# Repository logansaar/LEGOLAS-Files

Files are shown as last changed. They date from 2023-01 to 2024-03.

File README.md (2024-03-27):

# LEGOLAS-Files
Repository for LEGOLAS use files

LEGOLAS is the **LEGO** Based **L**ow-cost **A**utonomous **S**cientist

Maryland_LEGOLAS (1)

Please refer to Chapter 2 of this [thesis](https://github.com/logansaar/LEGOLAS-Files/blob/main/Saar%20Thesis%20Final%20Document.pdf) for a top-level overview of LEGOLAS construction, setup, and use: 

For inquiries regarding Python templates and educational worksheets that address additional active learning schemas, please contact:  takeuchi@umd.edu, aaron.kusne@nist.gov

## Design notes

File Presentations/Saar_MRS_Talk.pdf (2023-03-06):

# A Low-Cost

# Education Platform for Teaching Autonomous Physical Science

# Logan Saar

University of Maryland & NIST | 1

## Ichiro Takeuchi, Gilad Kusne, Austin McDannald

Senior - Materials Science and Engineering, UMD (lsaar@umd.edu)

MRS Symposium on Accelerating Experimental Materials Research with Machine Learning

# CAMEO: Closed-Loop Autonomous Materials Exploration and Optimization

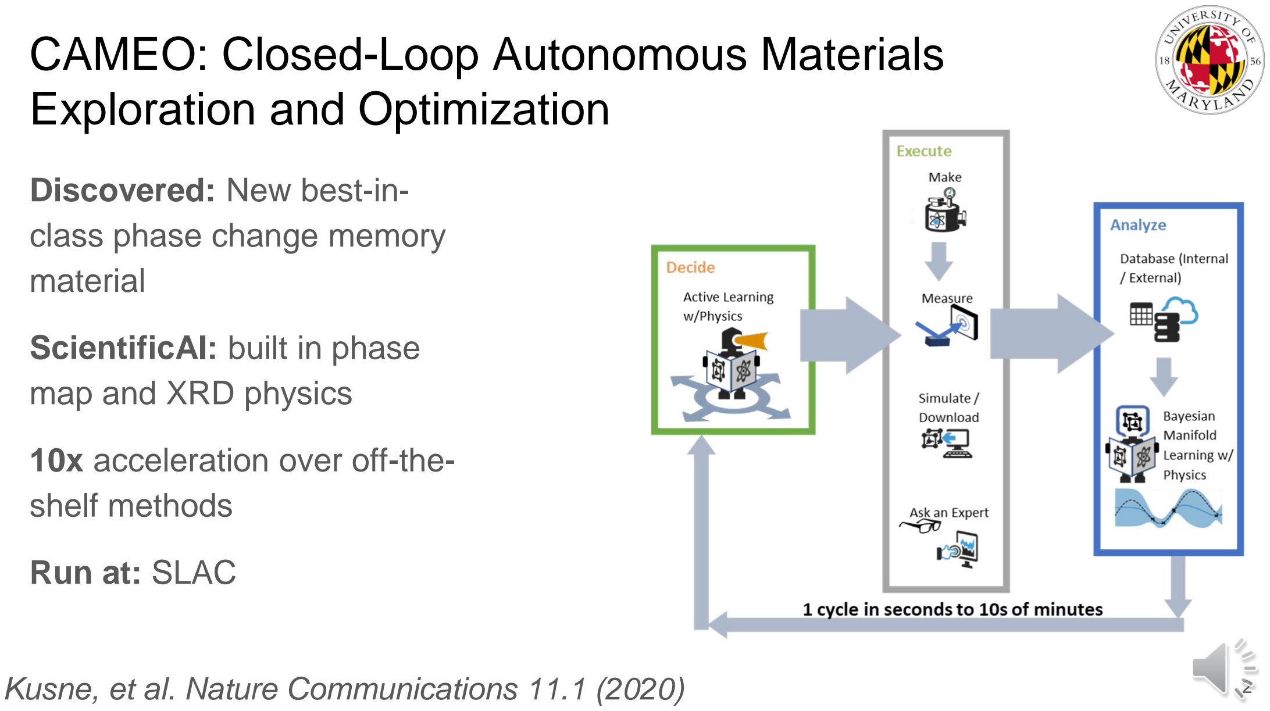
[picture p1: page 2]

## Discovered: New best-in-class phase change memory material

## ScientificAI: built in phase map and XRD physics

## 10x acceleration over off-the-shelf methods

## Run at: SLAC

### Kusne, et al. Nature Communications 11.1 (2020)

Burger, B., Maffettone, P.M., Gusev, V.V. et al. A mobile robotic chemist. Nature 583, 237–241 (2020)

Other Works

Stach, E., DeCost, B., Kusne, A. G., Hattrick-Simpers, J., Brown, K. A., Reyes, K. G., Schrier, J., Billinge, S., Buonassisi, T., Foster, I., Gomes, C. P., Gregoire, J. M., Mehta, A., Montoya, J., Olivetti, E., Park, C., Rotenberg, E., Saikin, S. K., Smullin, S., … Maruyama, B. (2021). Autonomous experimentation systems for materials development: A community perspective. Matter, 4(9), 2702-2726. https://doi.org/10.1016/j.matt.2021.06.036

# Low Cost Autonomous Physical Science System

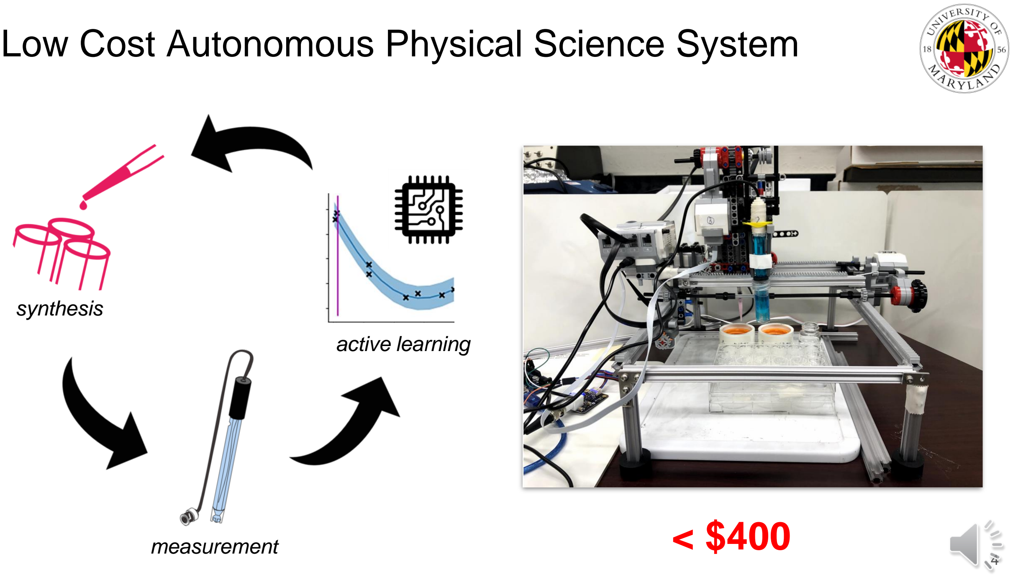
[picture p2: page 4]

measurement

synthesis

active learning

< $400

# Construction

Aluminum Frame

Lego Mindstorm
Components

Gerber, et al. (2017). Liquid-handling Lego robots and experiments for STEM education and research. PLOS Biology, 15(3)

# Synthesis Capabilities

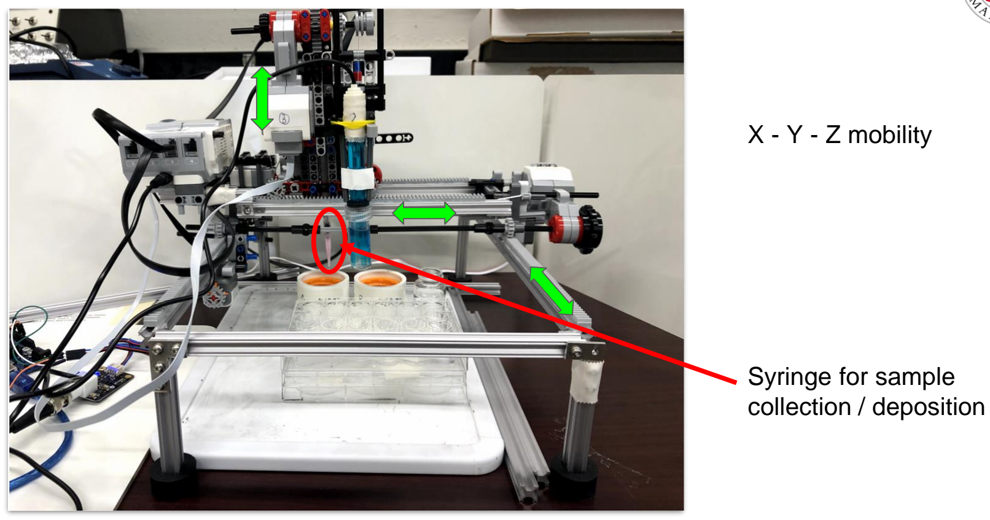
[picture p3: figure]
Syringe for sample collection / deposition; X - Y - Z mobility

# Measurement Capabilities

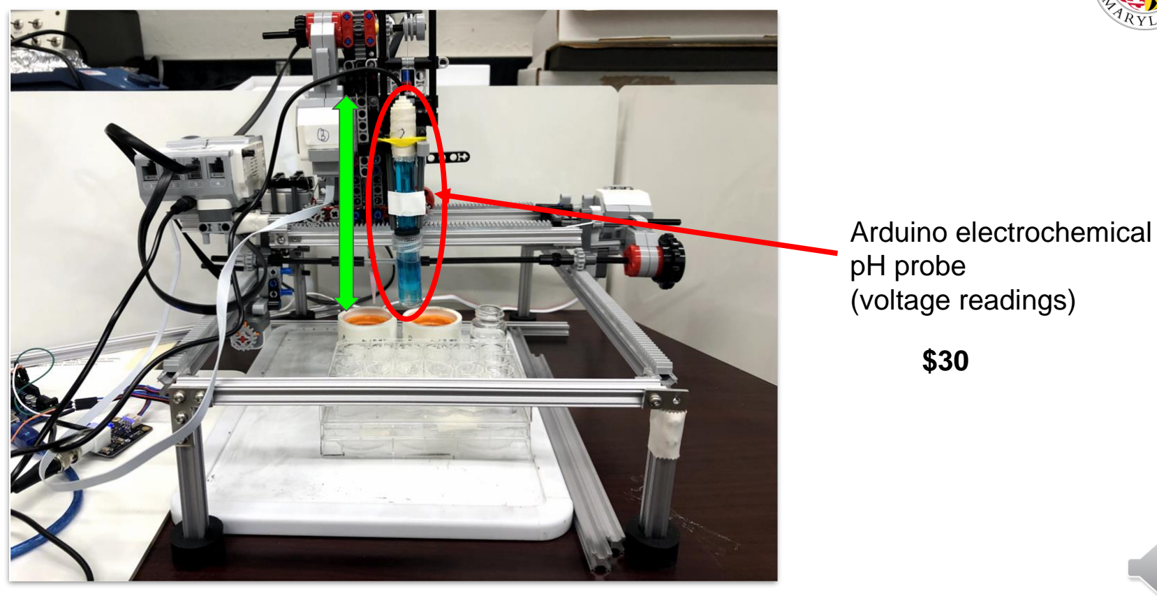
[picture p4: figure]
Arduino electrochemical pH probe (voltage readings)

# Setup and Control

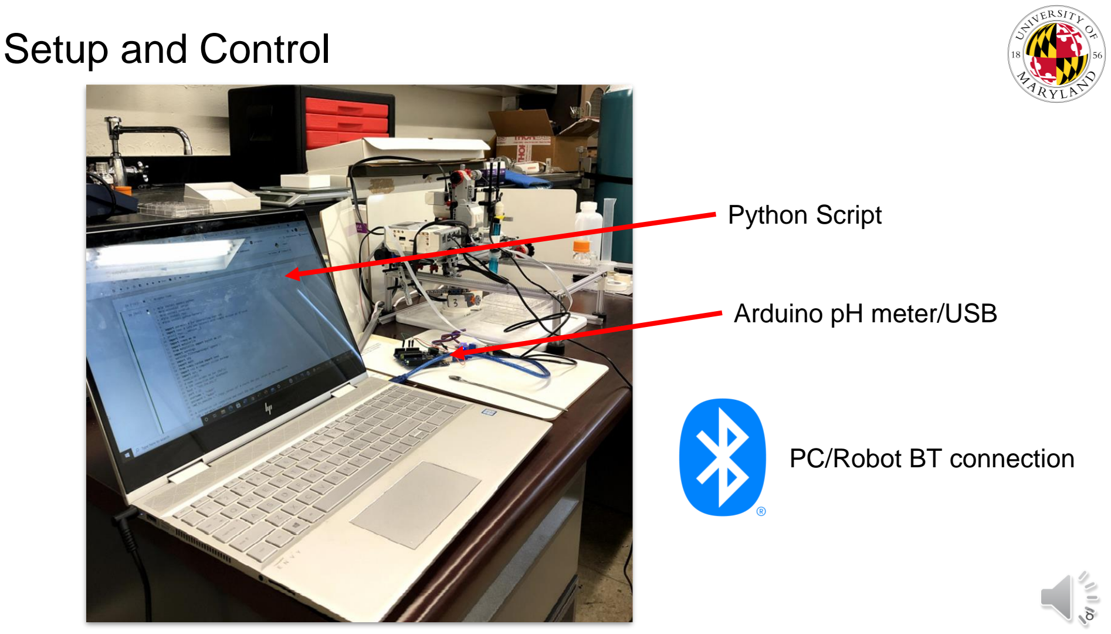
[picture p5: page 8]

Python Script

PC/Robot BT connection

Arduino pH meter/USB

# Exploring pH of Buffer Solutions

Composition Space
Weak Acid - Acetic Acid - 1 M
Conjugate Base - Sodium Acetate Solution - 1 M

Goal
Recover Henderson-Hasselbalch Equation.

## Henderson-Hasselbalch (HH) Equation:

Our known parameters
(for synthesis)

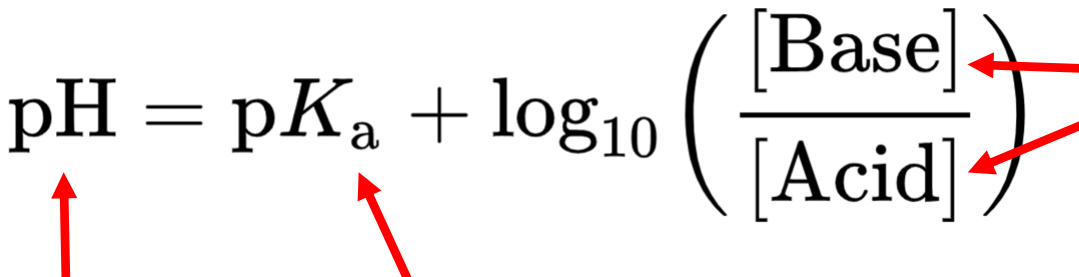
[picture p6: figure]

Response Variable
(measured)

Dissociation Constant
(unknown to robot)

# Active Learning Closed Loop System

- | Youtube Video Here | - (http://www.youtube.com/watch?v=Ul9sx29vAXE)

https://www.youtube.com/watch?v=Ul9sx29vAXE&t=1s

# Educational Application (Fall 2021 ENMA 437/637)

## UMD Machine Learning for Materials Science Course

## - 3 working systems - Teams of 5 students - Buffer Solution pH

- Gaussian Process
- Explore pH as f(composition)

## - Iodine Clock

# Model Determination

Can the Robot Determine the Physical Law by Itself?

# Can the Robot Discover the Physical Law?

## 1. Fit multiple functional forms to the data (“Candidates”)

## - (sinusoidal, power function, logarithmic, exponential, quadratic, etc.) - Non-linear least squares regression

x = [Acid]/[Base]

What is the correct form?

pH = A + B * log [C * (x-D) ] ? pH = A + B * sin [C * (x-D) ] ? pH = A + B * exp[C * (x-D) ] ? …

Alter parameters to get best fit

## 2. Create PDF for each candidate at every composition - (std. of PDF given by std. of residuals)

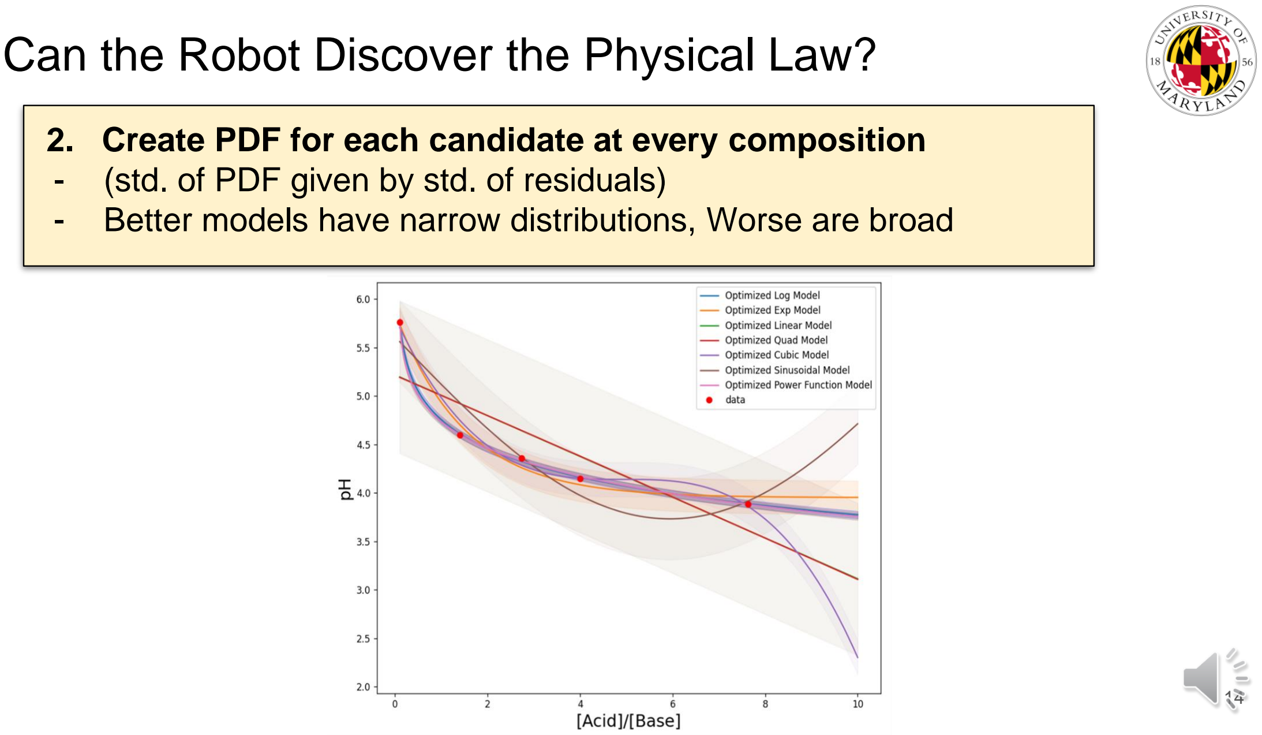
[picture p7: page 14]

## - Better models have narrow distributions, Worse are broad

# Can the Robot Discover the Physical Law?

## 3. Rank the likelihood that each candidate model produced the data

Performance Metric for
each candidate is the
sum of log(likelihood)
along every collected
data point

# Can the Robot Discover the Physical Law?

## 4. Determine which composition to measure next

# Yes, it did!

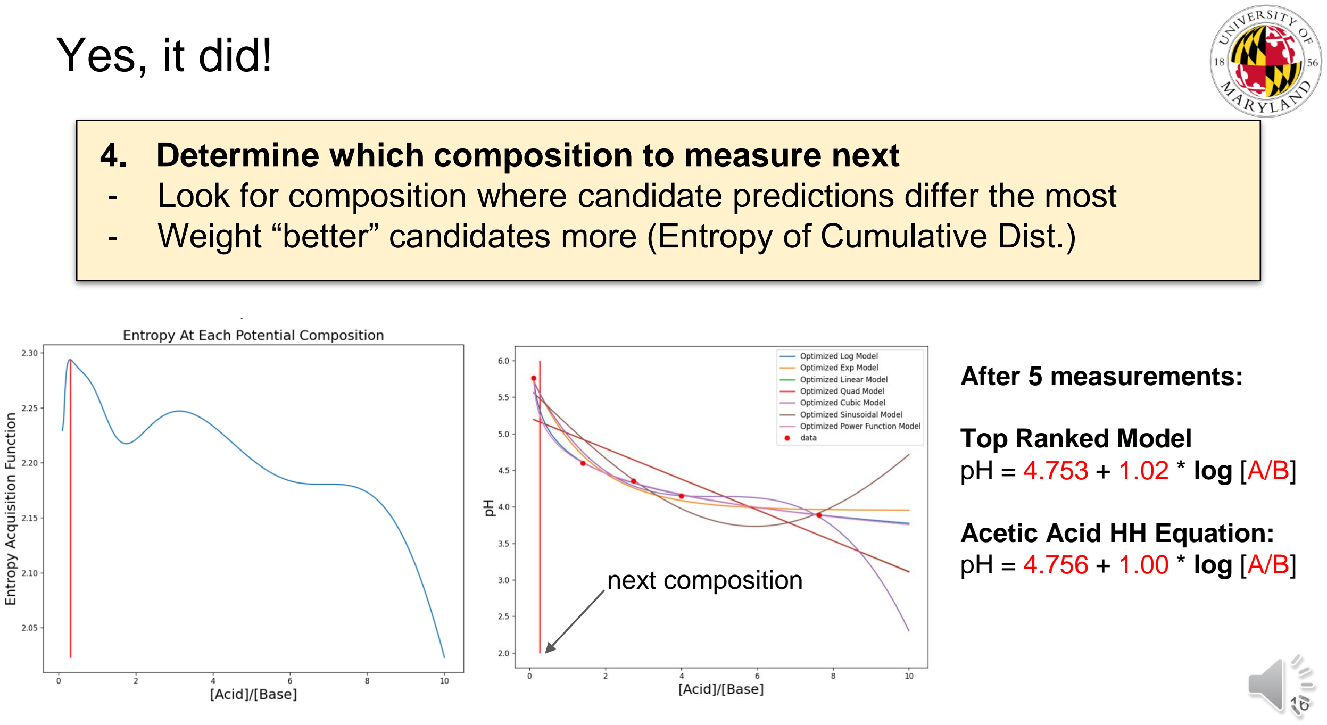
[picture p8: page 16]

## - Look for composition where candidate predictions differ the most - Weight “better” candidates more (Entropy of Cumulative Dist.)

next composition

After 5 measurements:

Top Ranked Model
pH = 4.753 + 1.02 * log [A/B]

Acetic Acid HH Equation:
pH = 4.756 + 1.00 * log [A/B]

# Summary

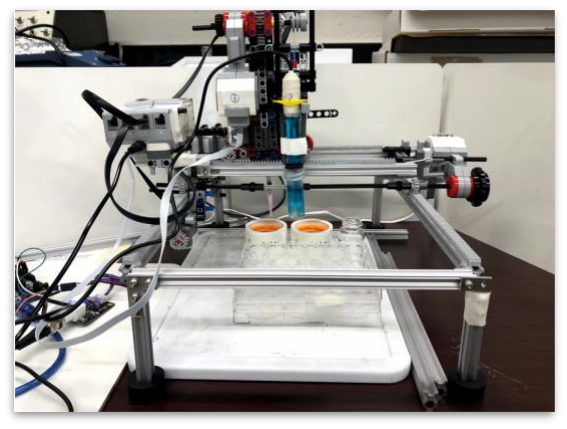
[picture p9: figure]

Closed Loop Autonomous Science System ➔ Educational Tool
➔ Low-cost
➔ Modular
➔ Materials Exploration

Used Gaussian Processes to explore pH as function of composition
➔ Flexible model
➔ Explore other active learning methods ...

# Acknowledgments

### Dr. Ichiro Takeuchi, PhD - UMD

### Dr. Gilad Kusne, PhD - NIST

### Dr. Austin McDannald, PhD - NIST

### Alex Wang - UMD

### Haotong Liang – UMD

### SURF Program – NIST

### MRS

## Email - lsaar@umd.edu

# References

Burger, B., Maffettone, P.M., Gusev, V.V. et al. A mobile robotic chemist. Nature 583, 237–241 (2020). https://doi.org/10.1038/s41586-020-2442-2

De Levie, R. (2003). The Henderson-hasselbalch equation: Its history and limitations. Journal of Chemical Education, 80(2), 146. https://doi.org/10.1021/ed080p146

Gerber, L. C., Calasanz-Kaiser, A., Hyman, L., Voitiuk, K., Patil, U., & Riedel-Kruse, I. H. (2017). Liquid-handling Lego robots and experiments for STEM education and research. PLOS Biology, 15(3), e2001413. https://doi.org/10.1371/journal.pbio.2001413

# Questions

# Appendix

## 4. Calculate the Entropy of the GMM at every composition

# Can the Robot Discover the Physical Law?

## - probability = (area under GMM likelihood curve)

## 4. Create a cumulative distribution of all PDFs at each composition

# Can the Robot Discover the Physical Law?

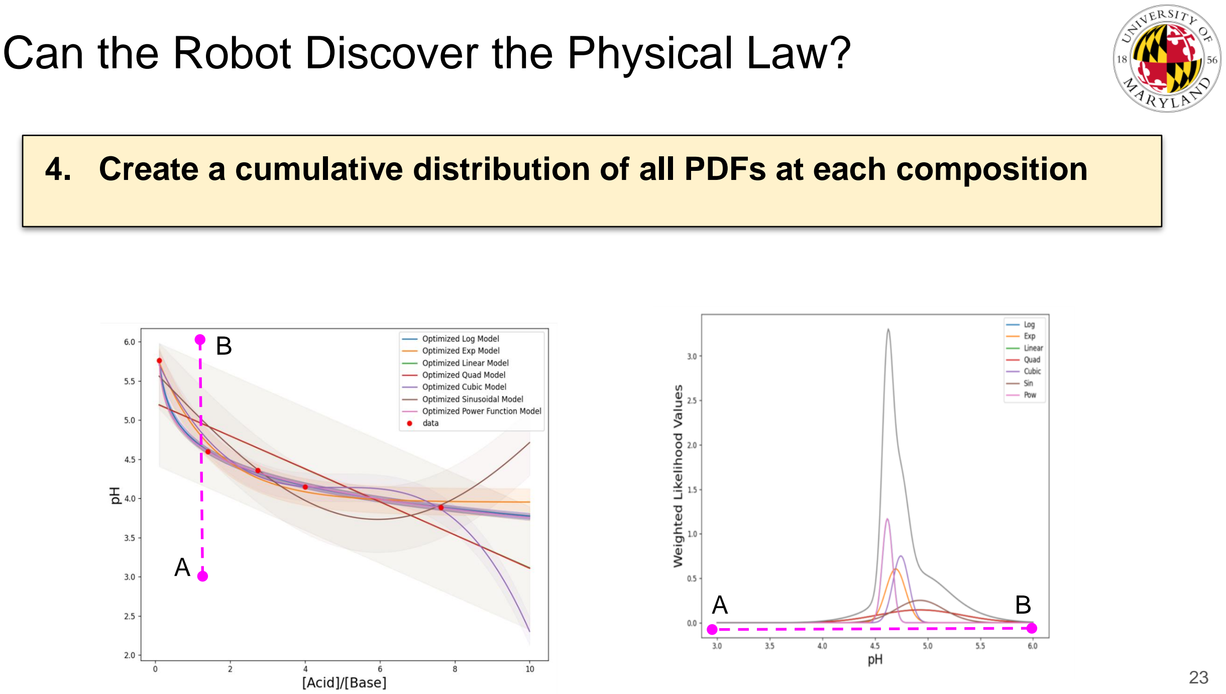
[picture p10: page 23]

A

B

A | B

# Exploration Initiative - (Gaussian Process)

Normal distribution of predicted pH for each potential % Acid composition

# Exploration Initiative - (Gaussian Process)

Kernel is a covariance function

# Exploration Initiative - (Gaussian Process)

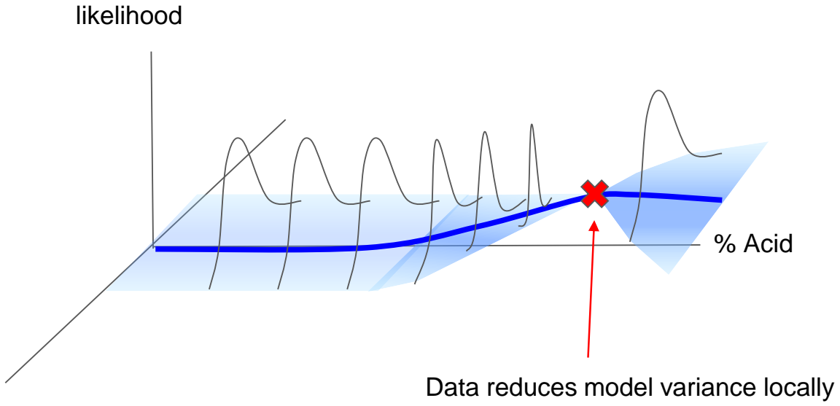
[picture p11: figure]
% Acid; likelihood; Data reduces model variance locally

pH

# Exploration Initiative - (Gaussian Process)

Active Learning:

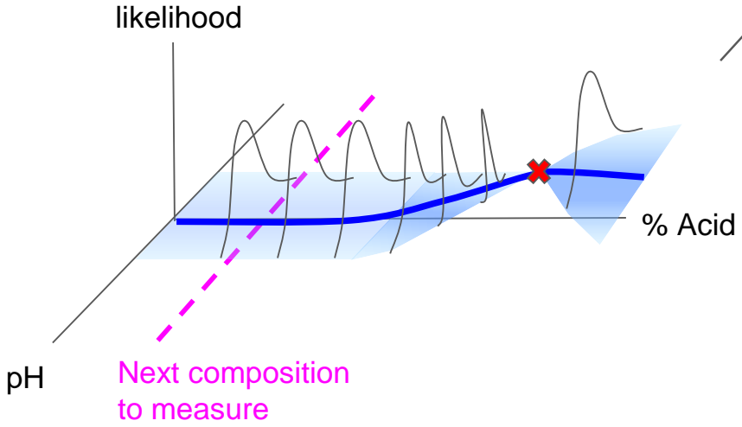
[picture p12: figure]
% Acid; likelihood; Next composition to measure

➔ Acquisition Function
➔ argmax (variance)
➔ Optimization initiative
➔ Scheduling of initiatives

# Autonomous Results - (Gaussian Process)

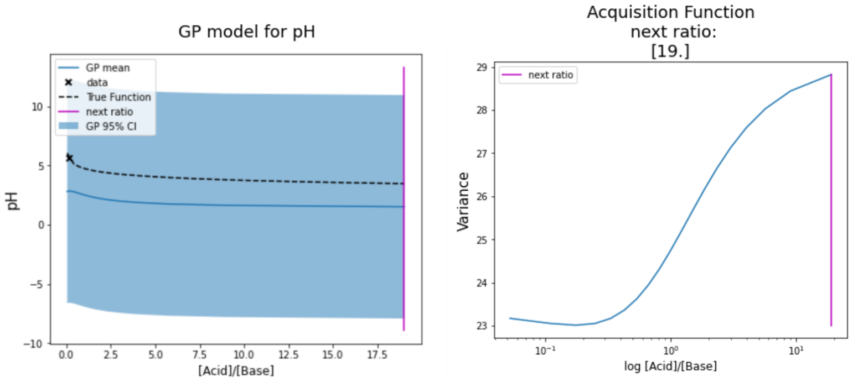
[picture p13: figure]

### 1 data point

# Autonomous Results - (Gaussian Process)

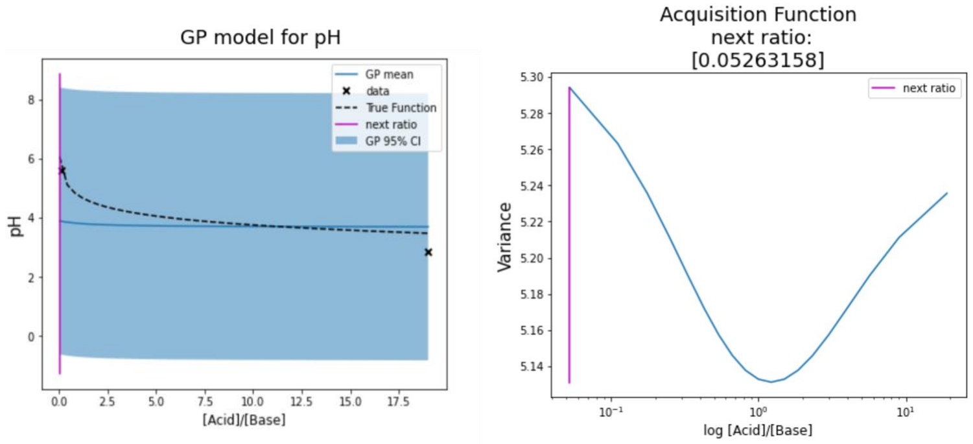
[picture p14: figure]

### 2 data points

# Autonomous Results - (Gaussian Process)

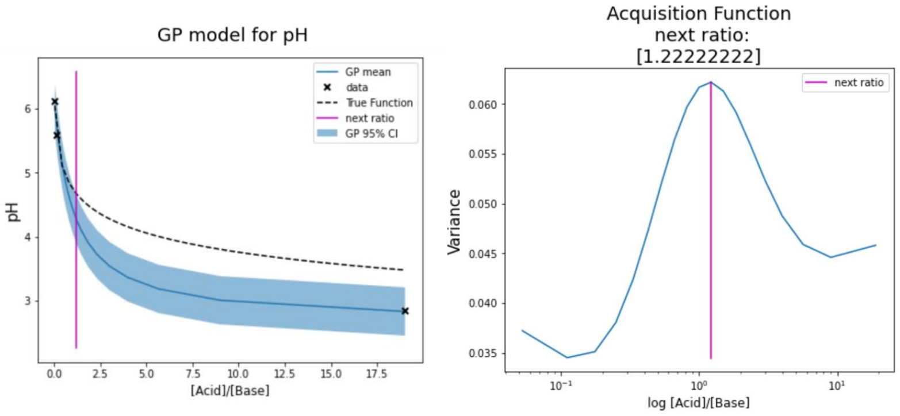
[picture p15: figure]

### 3 data points

# Autonomous Results - (Gaussian Process)

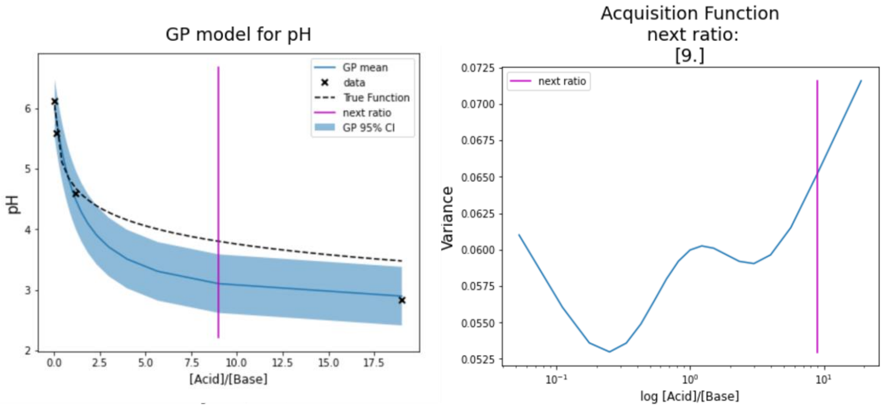
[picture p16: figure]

### 4 data points

# Autonomous Results - (Gaussian Process)

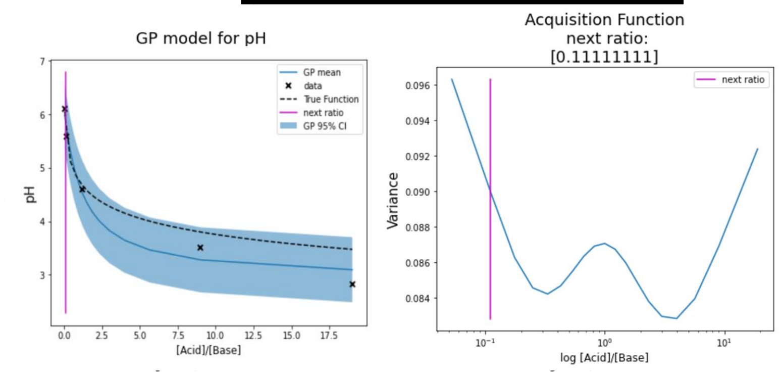
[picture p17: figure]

### 5 data points

# GP flexibility - (Gaussian Process)

HH equation relies on assumptions
➔ No self-ionization of water
➔ Valid only in certain composition range ➔ Our pKa ~ 4.7

# GP flexibility - (Gaussian Process)

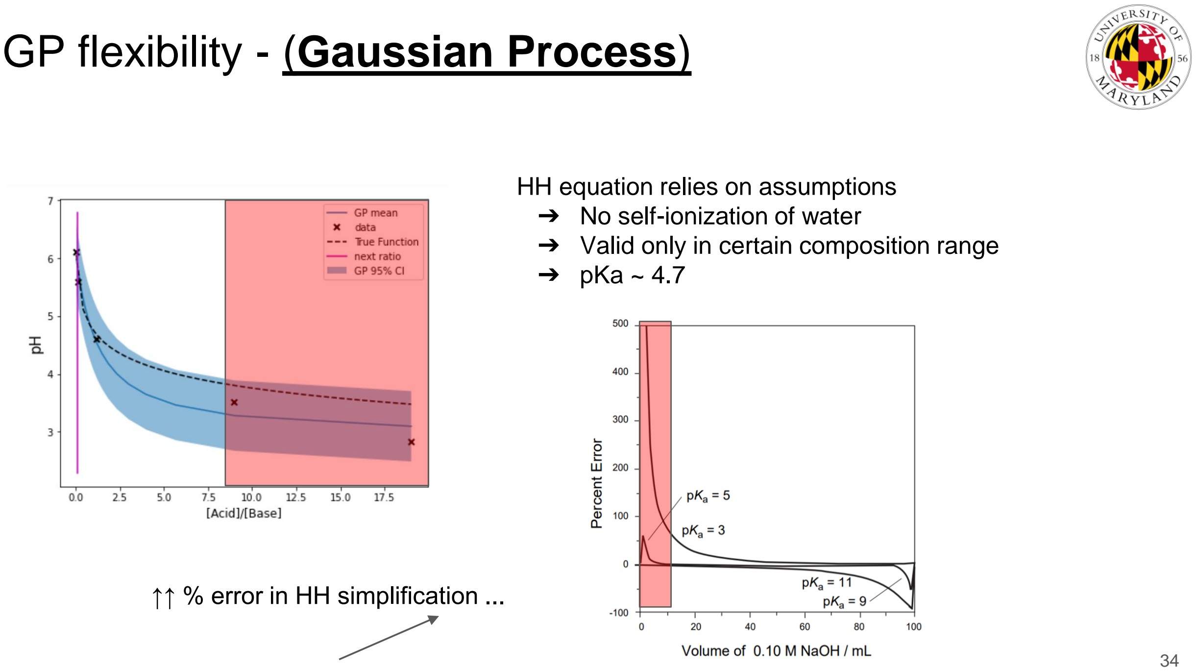
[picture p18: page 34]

HH equation relies on assumptions
➔ No self-ionization of water
➔ Valid only in certain composition range ➔ pKa ~ 4.7

↑↑ % error in HH simplification ...

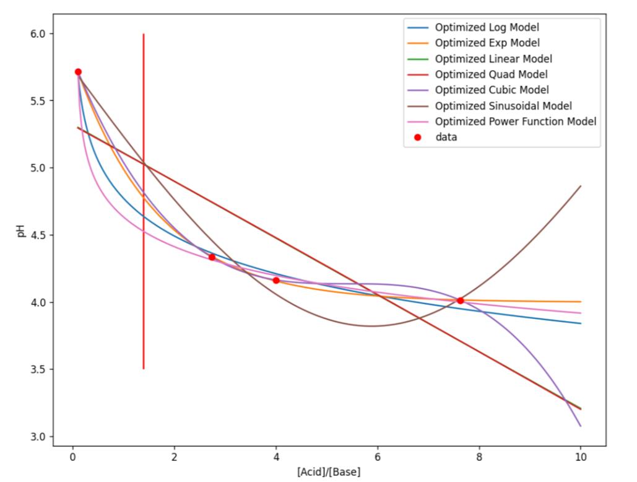
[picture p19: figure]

# Bayesian Inference

## Parameter Refinement

## Probabilistic interpretation … quantifying uncertainty (how confident are we?)

Bayes Theorem | P (model | data) = P(data | model) P(model) P(data)

# Brief Overview - Bayesian Machine Learning

## Probabilistic interpretation … quantifying uncertainty (how confident are we?)

Bayes Theorem | P (model | data) = P(data | model) P(model) P(data)

# Brief Overview - Bayesian Machine Learning

“Posterior” | “Prior”
Our confidence in this model being “correct” given the data (what we want to know) | Our confidence in this model being “correct” before getting data (assumption)

# Parameter Refinement - (Bayesian Inference)

## Prior: Assume model has logarithmic form (pH = A + B*log(C*x)) ➔ A, B, C are our model parameters

## Posterior: Probability of this model and its model parameters given the data

## Assume the model has a certain form

## Create parametric model with model parameters … (ex: model = A + B * x)

# Parameter Refinement - (Bayesian Inference)

## Problem: How to identify combination of parameters where posterior probability for model is greatest (i.e. best model?)

## Solution: Sample posterior distribution in parameter space using Markov Chain

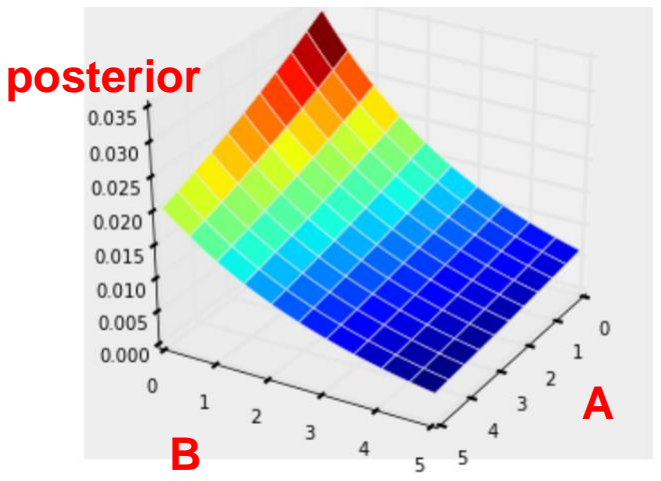
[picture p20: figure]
posterior

## Monte Carlo (MCMC) method A

Image Credit: https://nbviewer.jupyter.org/github/CamDavidsonPilon/Probabilistic-Programming-and-Bayesian-Methods-for-Hackers/blob/master/Chapter3_MCMC/Ch3_IntroMCMC_PyMC3.ipynb

## MCMC samples parameter space to find maxima in posterior (best model)

# Parameter Refinement - (Bayesian Inference)

## posterior

Example:

# Autonomous Results - (Bayesian Inference)

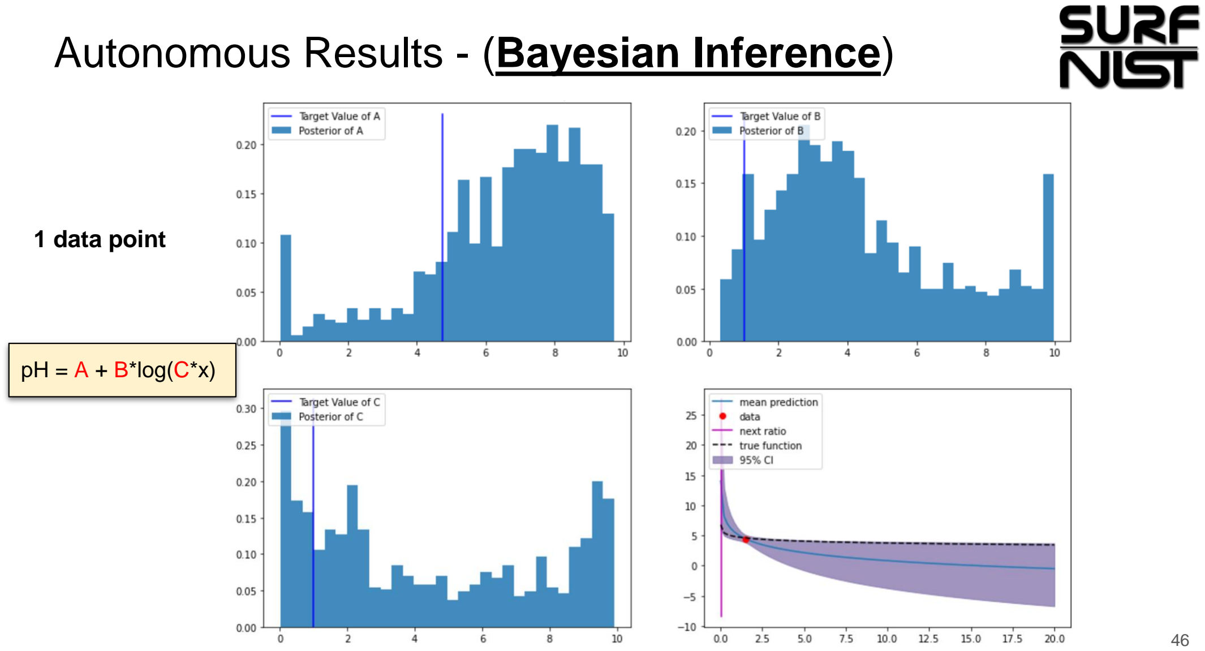
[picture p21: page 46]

### 1 data point

pH = A + B*log(C*x)

# Autonomous Results - (Bayesian Inference)

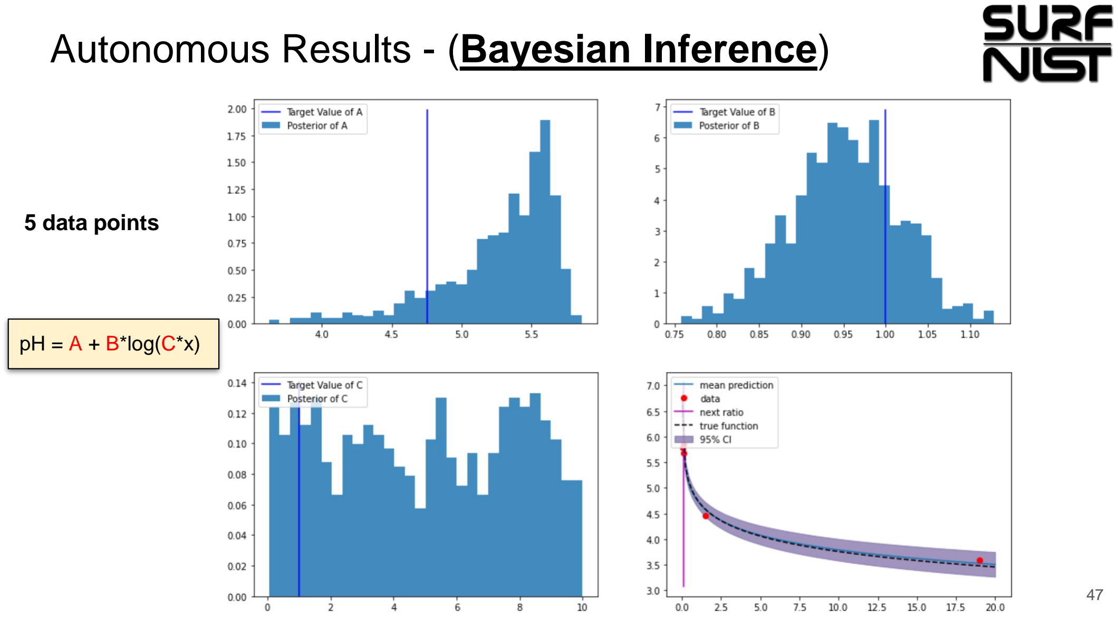
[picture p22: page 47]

### 5 data points

pH = A + B*log(C*x)

# The Next Steps:

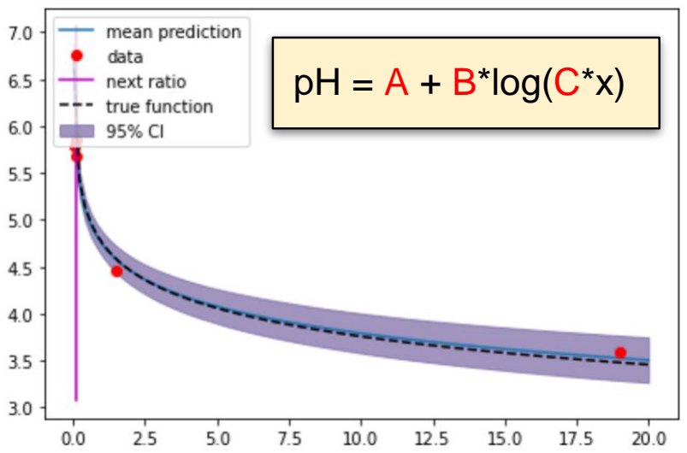
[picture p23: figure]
pH = A + B*log(C*x)

### For pH Measurement Setup

➔ Parameter Refinement

➔ Hypothesis Testing
➔ Bayesian methods
➔ Filter between candidate functions

## Other Applications (Educational Tool)

➔ Camera attachment
◆ Learn color mixing trends

## New data alters our prior beliefs → posterior beliefs

# Brief Overview - Bayesian Machine Learning

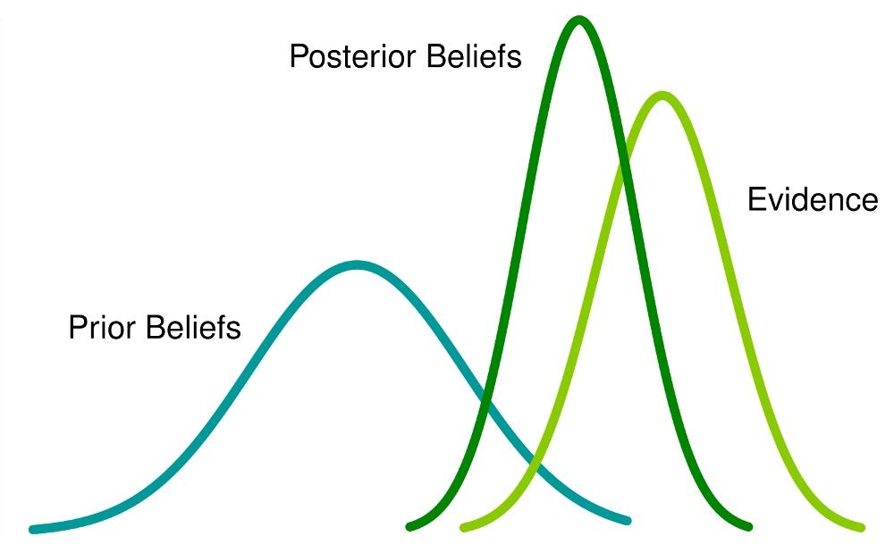
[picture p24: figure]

# Parameter Refinement - (Bayesian Inference)

## Produces posterior distributions for each model parameter

## Represent confidence in parameter values

## Active learning: [Parameter Refinement] → argmax (variance in model)

Example:

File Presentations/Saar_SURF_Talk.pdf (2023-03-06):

# Bayesian Active Learning for

# Autonomous Physical Science

# Logan Saar

Dr. Gilad Kusne (Mentor) - MML | 1

measurement

synthesis

active learning

# Motivation and Goals

# Composition - Property Relationships


### Optimize Performance → Properties → Composition

Image Credit: The four elements of materials science and engineering. (n.d.). https://www.nap.edu/read/758/chapter/3.

# Composition - Property Relationships

### Optimize Performance → Properties → Composition

Image Credit: The four elements of materials science and engineering. (n.d.). https://www.nap.edu/read/758/chapter/3.

# The Large Number Problem

σ

Element A
%B
0 | 50 | 100
Element B

# The Large Number Challenge


σ

Element A
%B
0 | 50 | 100
Element B

# The Large Number Challenge

σ

Element A
%B
0 | 50 | 100
Element B
Binary: | ~ 7,000
Tertiary: | ~ 250,000
Quaternary: ~ 7.6 million

Automated | Autonomous


Robot executes tasks | Robot reacts to input
Image Credit: https://blog.robotiq.com/a-brief-history-of-robots-in-manufacturing | Image Credit: Wired - Autonomous Cars

Automated | Autonomous

Robot reacts to ..
gathered data

ACTIVE LEARNING

Robot executes tasks


Burger, B., Maffettone, P.M., Gusev, V.V. et al. A mobile robotic chemist. Nature 583, 237–241 (2020)

# Low Cost Autonomous Physical Science System


11 measurement

synthesis

active learning

# Active Learning Closed Loop System

# Our Mission

Composition Space
Weak Acid - Acetic Acid - 1 M
Conjugate Base - Sodium Acetate Solution - 1 M

Goal
Recover Henderson-Hasselbalch Equation.

## Henderson-Hasselbalch (HH) Equation:

Our known parameters
(for synthesis)


Response Variable
(measured)

Dissociation Constant
(unknown to robot)

# Our Mission

Image Credit: https://www.easybiologyclass.com/titration-curve-of-a-weak-acid-and-its-pka-biochemistry-notes/

# Active Learning Closed Loop System - Our Robot

Aluminum Frame

## Construction

Lego Mindstorm
Components

Gerber, L. C. (2017). Liquid-handling Lego robots and experiments for STEM education and research. PLOS Biology, 15(3)

# Active Learning Closed Loop System - Our Robot

Syringe for sample collection / deposition (volume controlled); Sample Synthesis; X - Y - Z mobility

# Active Learning Closed Loop System - Our Robot

Measurement; Arduino electrochemical pH probe (voltage readings)

# Active Learning Closed Loop System - Our Robot

## Setup

Python Script

PC/Robot BT connection

Arduino pH meter/USB

# Active Learning Closed Loop System - Our Robot

## Process


Acid and base reservoirs

DI water (probe cleaning)

Plastic sample wells

# Active Learning Closed Loop System - Our Robot

Link Provided in Chat

- | Youtube Video Here | - (http://www.youtube.com/watch?v=Ul9sx29vAXE)

# Statistical Methods and Results

# Exploration Initiative - (Gaussian Process)

Normal distribution of predicted pH for each potential % Acid composition

% Acid; Likelihood of the model; 95% Confidence Interval; mean

# Exploration Initiative - (Gaussian Process)

pH

# Exploration Initiative - (Gaussian Process)

% Acid; likelihood; Next composition to measure

Active Learning:
➔ Acquisition Function
➔ argmax (variance)

# Autonomous Results - (Gaussian Process)


### 1 data point

# Autonomous Results - (Gaussian Process)


### 2 data points

# Autonomous Results - (Gaussian Process)


### 3 data points

# Autonomous Results - (Gaussian Process)


### 4 data points

# Autonomous Results - (Gaussian Process)


### 5 data points

# GP flexibility - (Gaussian Process)

HH equation relies on assumptions
➔ No self-ionization of water
➔ Valid only in certain composition range ➔ Our pKa ~ 4.7

# GP flexibility - (Gaussian Process)

HH equation relies on assumptions
➔ No self-ionization of water
➔ Valid only in certain composition range ➔ pKa ~ 4.7

↑↑ % error in HH simplification ...

# Summary


Closed Loop Autonomous Science System ➔ Educational Tool
➔ Low-cost
➔ Modular
➔ Materials Exploration

Used Gaussian Processes to explore pH as function of composition
➔ Flexible model
➔ Explore other active learning methods ...

# Acknowledgments

### Dr. Gilad Kusne, PhD

### Dr. Ichiro Takeuchi, PhD

### Dr. Austin McDannald, PhD

### Alex Wang

### Haotong Liang

# Questions

# References

Burger, B., Maffettone, P.M., Gusev, V.V. et al. A mobile robotic chemist. Nature 583, 237–241 (2020). https://doi.org/10.1038/s41586-020-2442-2

De Levie, R. (2003). The Henderson-hasselbalch equation: Its history and limitations. Journal of Chemical Education, 80(2), 146. https://doi.org/10.1021/ed080p146

Gerber, L. C., Calasanz-Kaiser, A., Hyman, L., Voitiuk, K., Patil, U., & Riedel-Kruse, I. H. (2017). Liquid-handling Lego robots and experiments for STEM education and research. PLOS Biology, 15(3), e2001413. https://doi.org/10.1371/journal.pbio.2001413

# Appendix

# The Next Steps:

pH = A + B*log(C*x)

### For pH Measurement Setup

➔ Parameter Refinement

➔ Hypothesis Testing
➔ Bayesian methods
➔ Filter between candidate functions

## Other Applications (Educational Tool)

➔ Camera attachment
◆ Learn color mixing trends

# Exploration Initiative - (Gaussian Process)

% Acid; Likelihood of the model; mean; Many models generated: ➔ Non-parametric ➔ Flexible ➔ Averaged ➔ Kernel determines “smoothness” ➔ Noise tolerant

Kernel is a covariance function

## Probabilistic interpretation … quantifying uncertainty (how confident are we?)

Bayes Theorem | P (model | data) = P(data | model) P(model) P(data)

# Brief Overview - Bayesian Machine Learning

## Probabilistic interpretation … quantifying uncertainty (how confident are we?)

Bayes Theorem | P (model | data) = P(data | model) P(model) P(data)

# Brief Overview - Bayesian Machine Learning

“Posterior” | “Prior”
Our confidence in this model being “correct” given the data (what we want to know) | Our confidence in this model being “correct” before getting data (assumption)

## New data alters our prior beliefs → posterior beliefs

# Brief Overview - Bayesian Machine Learning

## Assume the model has a certain form Create parametric model with model parameters … (ex: model = A + B * x)

# Parameter Refinement - (Bayesian Inference)

## Problem: How to identify combination of parameters where posterior probability for model is greatest (i.e. best model?)

## Solution: Sample posterior distribution in parameter space using Markov Chain

posterior

## Monte Carlo (MCMC) method A

Image Credit: https://nbviewer.jupyter.org/github/CamDavidsonPilon/Probabilistic-Programming-and-Bayesian-Methods-for-Hackers/blob/master/Chapter3_MCMC/Ch3_IntroMCMC_PyMC3.ipynb

## MCMC samples parameter space to find maxima in posterior (best model)

# Parameter Refinement - (Bayesian Inference)

## posterior

Example:

# Parameter Refinement - (Bayesian Inference)

## Produces posterior distributions for each model parameter

Posterior of A; Posterior of B

## Represent confidence in parameter values

## Active learning: [Parameter Refinement] → argmax (variance in model)

Example:

# Parameter Refinement - (Bayesian Inference)

## Prior: Assume model has logarithmic form (pH = A + B*log(C*x))

## Posterior: Probability of this model and its model parameters given the data

# Autonomous Results - (Bayesian Inference)


### 1 data point

pH = A + B*log(C*x)

# Autonomous Results - (Bayesian Inference)


### 5 data points

pH = A + B*log(C*x)

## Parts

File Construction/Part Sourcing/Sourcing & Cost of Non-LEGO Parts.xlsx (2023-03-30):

Vendor | Description | URL | Unit Price ($) | Quantity | Net Price | Summary
MakerBeam | 300 mm Anodised Al Extrusion (Black - 4 piece) | https://www.makerbeam.com/makerbeam-300mm-4p-black-makerbeam.html | $12.03 | 2 | $24.07 | Frame Components ... Price per Robot ~ $100
MakerBeam | 3D printed End Caps (Black - 4 piece) | https://www.makerbeam.com/makerbeam-3d-printed-end-caps-for-makerbeam-4p.html?id=24117793 | $4.99 | 1 | $4.99
MakerBeam | Corner Cubes (Black - 12 piece w/ screws) | https://www.makerbeam.com/makerbeam-corner-cubes-12p-black-for-makerbeam.html?id=24117589 | $18.85 | 1 | $18.85
MakerBeam | 90 degree L-Brackets (12-piece) | https://www.makerbeam.com/makerbeam-90-degree-brackets-12p.html?id=24117637 | $7.30 | 1 | $7.30
MakerBeam | T-slot Nuts (25-piece) | https://www.makerbeam.com/makerbeam-t-slot-nuts-for-makerbeam-25p.html?id=24117835 | $15.73 | 2 | $31.46
MakerBeam | 6-mm M3 Wing Bolts (100 pack) | https://www.makerbeam.com/makerbeam-wing-type-bolts-6mm-100p-for-makerbeam.html | $11.53 | 1 | $11.53
CanaKit | R-Pi Buildhat | https://www.canakit.com/raspberry-pi-build-hat.html | $25 | 2 | $50 | Non-Lego Electronics ... Price per Robot ~ $470
DigiKey | R-Pi Buildhat Chargers (Australian Plug) | https://www.digikey.com/en/products/detail/raspberry-pi/SC0749/15298150?src=raspberrypi | $15 | 2 | $30
DF Robot | Arduino pH Sensors | https://www.dfrobot.com/product-1025.html | $29.50 | 1 | $29.50
Amazon | R-Pi 4GB 64 bit | https://www.amazon.com/CanaKit-Raspberry-Pi-Extreme-Kit/dp/B09W7P91SP?hvadid=598359365939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 | $139.99 | 2 | $279.98
Amazon | Plug Adapter (US - Aus) | https://www.amazon.com/Unidapt-Adapter-Grounded-Adaptor-Converter/dp/B08D741PV6?hvadid=459618435588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 | $7.99 | 2 | $15.98
Amazon | Arduino Uno | https://www.amazon.com/gp/product/B008GRTSV6?camp=1789&creative=9325&creativeASIN=B008GRTSV6&linkId=d7b55cbe1aae09827d7c156218cf0efb | $28.50 | 1 | $28.50
Amazon | USB 2.0 A Male to B Male | https://www.amazon.com/Monoprice-1-5-Feet-24AWG-Plated-105436/dp/B009GUVZOK?hvadid=309773039951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 | $3.96 | 1 | $3.96
Amazon | Digital Scale (mg accuracy) | https://www.amazon.com/Milligram-Calibration-Tweezers-Weighing-Included/dp/B09NQ4RGHC?hvadid=564700665543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 | $18.58 | 1 | $18.58
Amazon | Jumper Wire Cables | https://www.amazon.com/Practical-Durable-Breadboard-Connecting-Prototyping/dp/B09XDL1JFG | $3.37 | 1 | $3.37
Ali Express | WeDo Extension Cables for LEGO | https://www.aliexpress.us/item/3256801836960111.html?_t=pvid%3Ab7549926-05dc-4d5d-8cc6-c14974441944&_randl_shipto=US | $6.11 | 1 | $6.11
Amazon | Chem Lab Stands and Rings (1 pack) | https://www.amazon.com/QWORK-Laboratory-Stands-Support-Burette/dp/B08ZSC1H5F | $19.97 | 1 | $19.97 | Chemistry Equipment ... Price per Robot ~ $40
Amazon | 1 mL/cc syringes (10 pack) | https://www.amazon.com/Measuring-Individually-Measurement-Scientific-Applicator/dp/B08T175QFR?s=industrial | $6.99 | 1 | $6.99
Adh. Disp. LTD | 20 guage dispensing tips (50 pack) | https://www.adhesivedispensing.net/TN20_Tapered_Tip_pink_pk_50_p/tn20.htm | $10.00 | 1 | $10.00
NEST | 24 Well Cell Culture Plates (~1cm diameter) | https://www.nest-biotech.com/cell-culture-plates/59174695.html | $5.00 | 1 | $5.00
 |  |  |  | Cost Per Robot | $584.14

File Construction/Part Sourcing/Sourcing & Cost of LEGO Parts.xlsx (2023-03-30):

LdrawID | Part | Color | Qty | Total Price | Link
11955 | Technic, Gear 8 Tooth with Dual Face without Friction | Dark Gray | 1 | $0.35 | https://www.lego.com/en-us/pick-and-build/pick-a-brick?query=11955&page=1
13971 | Wheel 18mm D. x 8mm with Fake Bolts and Deep Spokes with Inner Ring | Light Bluish Gray | 1 | $0.20 | https://www.lego.com/en-us/pick-and-build/pick-a-brick?query=13971&page=1
15100 | Technic, Pin with Friction Ridges and Pin Hole | White | 1 | $0.22 | https://www.toypro.com/us/product/35713/technic-pin-with-friction-ridges-lengthwise-and-pin-hole/white
24316 | Technic, Axle 3L with Stop | Reddish Brown | 3 | $0.21 | https://www.lego.com/en-us/pick-and-build/pick-a-brick?query=24316&page=1
2780 | Technic, Pin with Short Friction Ridges | Black | 64 | $3.84 | https://www.lego.com/en-us/pick-and-build/pick-a-brick?query=2780&page=1
32009 | Technic, Liftarm, Modified Bent Thick 1 x 11.5 Double | Light Bluish Gray | 2 | $0.70 | https://www.toypro.com/us/product/481/technic-liftarm-1-x-11-5-double-bent-thick/light-bluish-gray
32073 | Technic, Axle 5L | White | 1 | $0.11 | https://www.lego.com/en-us/pick-and-build/pick-a-brick?query=32073&page=1
32073 | Technic, Axle 5L | Black | 1 | $0.11 | https://www.lego.com/en-us/pick-and-build/pick-a-brick?query=32073&page=1
4265c | Technic Bush 1/2 Smooth | Light Bluish Gray | 2 | $0.10 | https://www.toypro.com/us/product/1966/technic-bush-1-2-smooth/light-bluish-gray
44 | Technic, Axle and Pin Connector Toggle Joint Smooth | Red (Link is White) | 1 | $0.50 | https://www.toypro.com/us/product/26390/technic-axle-and-pin-connector-toggle-joint-smooth/white
32140 | Technic, Liftarm, Modified Bent Thick L-Shape 2 x 4 | White (Link is Bluish Gray) | 3 | $0.42 | https://www.toypro.com/us/product/1125/technic-liftarm-2-x-4-l-shape-thick/light-bluish-gray
32140 | Technic, Liftarm, Modified Bent Thick L-Shape 2 x 4 | Light Bluish Gray | 2 | $0.28 | https://www.toypro.com/us/product/1125/technic-liftarm-2-x-4-l-shape-thick/light-bluish-gray
32184 | Technic, Axle and Pin Connector Perpendicular 3L with Center Pin Hole | Black | 4 | $0.56 | https://www.toypro.com/us/product/1395/technic-axle-and-pin-connector-perpendicular-3l-with-center-pin-hole/black
32269 | Technic, Gear 20 Tooth Double Bevel | Tan | 4 | $1.84 | https://www.toypro.com/us/product/1506/technic-gear-20-tooth-double-bevel/tan
32270 | Technic, Gear 12 Tooth Double Bevel | Light Bluish Gray | 4 | $0.72 | https://www.lego.com/en-us/pick-and-build/pick-a-brick?query=32270&page=1
32278 | Technic, Liftarm Thick 1 x 15 | White (Link is Bluish Gray) | 3 | $1.98 | https://www.toypro.com/us/product/1483/technic-liftarm-1-x-15-thick/dark-bluish-gray
32278 | Technic, Liftarm Thick 1 x 15 | Light Bluish Gray (Link is Dark Grey) | 1 | $0.66 | https://www.toypro.com/us/product/1483/technic-liftarm-1-x-15-thick/dark-bluish-gray
32316 | Technic, Liftarm Thick 1 x 5 | Black | 1 | $0.19 | https://www.lego.com/en-us/pick-and-build/pick-a-brick?query=32316&page=1
32316 | Technic, Liftarm Thick 1 x 5 | Light Bluish Gray | 3 | $0.57 | https://www.lego.com/en-us/pick-and-build/pick-a-brick?query=32316&page=1
32523 | Technic, Liftarm Thick 1 x 3 | Black | 3 | $0.30 | https://www.lego.com/en-us/pick-and-build/pick-a-brick?query=32523&page=1
32523 | Technic, Liftarm Thick 1 x 3 | White | 3 | $0.30 | https://www.lego.com/en-us/pick-and-build/pick-a-brick?query=32523&page=1
32523 | Technic, Liftarm Thick 1 x 3 | Light Bluish Gray | 1 | $0.10 | https://www.lego.com/en-us/pick-and-build/pick-a-brick?query=32523&page=1
32524 | Technic, Liftarm Thick 1 x 7 | Black | 1 | $0.25 | https://www.lego.com/en-us/pick-and-build/pick-a-brick?query=32524&page=1
32524 | Technic, Liftarm Thick 1 x 7 | White | 2 | $0.50 | https://www.lego.com/en-us/pick-and-build/pick-a-brick?query=32524&page=1
32524 | Technic, Liftarm Thick 1 x 7 | Light Bluish Gray | 3 | $0.75 | https://www.lego.com/en-us/pick-and-build/pick-a-brick?query=32524&page=1
32525 | Technic, Liftarm Thick 1 x 11 | White | 2 | $0.76 | https://www.toypro.com/us/product/4719/technic-liftarm-1-x-11-thick/white
32526 | Technic, Liftarm, Modified Bent Thick L-Shape 3 x 5 | Black | 7 | $1.68 | https://www.lego.com/en-us/pick-and-build/pick-a-brick?query=32526&page=1
32526 | Technic, Liftarm, Modified Bent Thick L-Shape 3 x 5 | White | 1 | $0.24 | https://www.lego.com/en-us/pick-and-build/pick-a-brick?query=32526&page=1
3707 | Technic, Axle 8L | White | 2 | $0.44 | https://www.lego.com/en-us/pick-and-build/pick-a-brick?query=3707&page=1
3708 | Technic, Axle 12L | Black | 11 | $2.97 | https://www.lego.com/en-us/pick-and-build/pick-a-brick?query=3708&page=1
3713 | Technic Bush | Light Bluish Gray | 13 | $1.30 | https://www.toypro.com/us/product/968/technic-bush/light-bluish-gray
37312c01 | Electric Sensor, Force - SPIKE Prime | Black | 2 | $63.90 | https://education.lego.com/en-us/products/lego-technic-force-sensor/45606?s_kwcid=AL!790!3!!!!x!!&mtm_medium=SEM
3743 | Technic, Gear Rack 1 x 4 | Light Bluish Gray | 43 | $8.17 | https://www.lego.com/en-us/pick-and-build/pick-a-brick?query=3743&page=1
3749 | Technic, Axle 1L with Pin without Friction Ridges | Tan | 2 | $0.14 | https://www.toypro.com/us/product/1152/technic-axle-pin-without-friction-ridges-lengthwise/tan
39367c02 | Wheel 56 x 14 Technic with Axle Hole and 8 Pin Holes with Fixed Black Rubber Tire | Black | 1 | $2.76 | https://www.toypro.com/us/product/40878/wheel-56-x-14-technic-with-axle-hole-and-8-pin-holes-with-fixed-black-rubber-tire/black
39790 | Technic, Liftarm, Modified Frame Thick 11 x 15 Open Center | Black | 1 | $2.14 | https://www.lego.com/en-us/pick-and-build/pick-a-brick?query=39790&page=1
41239 | Technic, Liftarm Thick 1 x 13 | Light Bluish Gray | 2 | $0.78 | https://www.lego.com/en-us/pick-and-build/pick-a-brick?query=41239&page=1&filters.i0.values.i0=pab
42003 | Technic, Axle and Pin Connector Perpendicular 3L with 2 Pin Holes | Red | 2 | $0.38 | https://www.toypro.com/us/product/3449/technic-axle-and-pin-connector-perpendicular-3l-with-2-pin-holes/red
42003 | Technic, Axle and Pin Connector Perpendicular 3L with 2 Pin Holes | Black | 2 | $0.28 | https://www.toypro.com/us/product/1916/technic-axle-and-pin-connector-perpendicular-3l-with-2-pin-holes/black
43093 | Technic, Axle 1L with Pin with Friction Ridges | Blue | 8 | $0.88 | https://www.toypro.com/us/product/1664/technic-axle-pin-with-friction-ridges-lengthwise/blue
44294 | Technic, Axle 7L | Light Bluish Gray | 2 | $0.32 | https://www.lego.com/en-us/pick-and-build/pick-a-brick?query=44294&page=1&filters.i0.values.i0=pab
4519 | Technic, Axle 3L | White | 1 | $0.05 | https://www.lego.com/en-us/pick-and-build/pick-a-brick?query=4519&page=1
48989 | Technic, Pin Connector Perpendicular 3L with 4 Pins | Light Bluish Gray | 9 | $1.80 | https://www.toypro.com/us/product/1928/technic-pin-connector-perpendicular-3l-with-4-pins/light-bluish-gray
54696c01 | Electric, Motor SPIKE Prime, Medium Angular | Light Bluish Gray | 5 | $214.75 | https://education.lego.com/en-us/products/lego-technic-medium-angular-motor/45603?s_kwcid=AL!790!3!!!!x!!&mtm_medium=SEM
56903 | Wheel 18mm D. x 8mm with Fake Bolts and Shallow Spokes and Axle Hole | White | 1 | $0.32 | https://www.lego.com/en-us/pick-and-build/pick-a-brick?query=56903&page=1
6538c | Technic, Axle Connector 2L (Smooth with x Hole + Orientation) | White | 7 | $1.26 | toypro.com/us/product/36700/technic-axle-connector-smooth-with-x-hole-orientation/white
60479 | Plate 1 x 12 | White | 1 | $0.23 | https://www.lego.com/en-us/pick-and-build/pick-a-brick?query=60479&page=1
60484 | Technic, Liftarm, Modified T-Shape Thick 3 x 3 | White | 1 | $0.18 | https://www.lego.com/en-us/pick-and-build/pick-a-brick?query=60484&page=1
60485 | Technic, Axle 9L | Yellow | 2 | $0.40 | https://www.lego.com/en-us/pick-and-build/pick-a-brick?query=60485&page=1
63869 | Technic, Axle and Pin Connector Perpendicular Triple | Light Bluish Gray | 2 | $0.46 | https://www.toypro.com/us/product/1452/technic-axle-and-pin-connector-perpendicular-triple/light-bluish-gray
64178 | Technic, Liftarm, Modified Frame Thick 5 x 11 Open Center | Light Bluish Gray | 1 | $1.24 | https://www.lego.com/en-us/pick-and-build/pick-a-brick?query=64178&page=1
64179 | Technic, Liftarm, Modified Frame Thick 5 x 7 Open Center | Light Bluish Gray | 4 | $3.56 | https://www.lego.com/en-us/pick-and-build/pick-a-brick?query=64179&page=1
64179 | Technic, Liftarm, Modified Frame Thick 5 x 7 Open Center | Black | 1 | $0.89 | https://www.lego.com/en-us/pick-and-build/pick-a-brick?query=64179&page=1
64781 | Technic, Gear Rack 1 x 13 with Axle and Pin Holes | Black | 2 | $4.20 | https://www.toypro.com/us/product/2322/technic-gear-rack-1-x-13-with-axle-and-pin-holes/black
6536 | Technic, Axle and Pin Connector Perpendicular | Red | 1 | $0.15 | https://www.toypro.com/us/product/1008/technic-axle-and-pin-connector-perpendicular/red
6558 | Technic, Pin 3L with Friction Ridges | Blue | 30 | $1.80 | https://www.lego.com/en-us/pick-and-build/pick-a-brick?query=6558&page=1
87082 | Technic, Pin 3L with Friction Ridges and Center Pin Hole | Light Bluish Gray | 2 | $0.36 | https://www.toypro.com/us/product/2210/technic-pin-long-with-friction-ridges-lengthwise-and-center-pin-hole/light-bluish-gray
94925 | Technic, Gear 16 Tooth (Second Version - Reinforced) | Light Bluish Gray | 12 | $2.40 | https://www.lego.com/en-us/pick-and-build/pick-a-brick?query=94925&page=1
 |  |  | Total: | $336.95

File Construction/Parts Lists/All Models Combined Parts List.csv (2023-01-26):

BLItemNo | ElementId | LdrawId | PartName | BLColorId | LDrawColorId | ColorName | ColorCategory | Qty | Weight
11955 |  | 11955 | Technic, Gear 8 Tooth with Dual Face without Friction | 10 | 8 | Dark Gray | Solid Colors | 1 | 0.2
13971 | 6044729 | 13971 | Wheel 18mm D. x 8mm with Fake Bolts and Deep Spokes with Inner Ring | 86 | 71 | Light Bluish Gray | Solid Colors | 1 | 1.02
15100 | 6282148 | 15100 | Technic, Pin with Friction Ridges and Pin Hole | 1 | 15 | White | Solid Colors | 1 | 0.4
24316 | 6135494 | 24316 | Technic, Axle 3L with Stop | 88 | 70 | Reddish Brown | Solid Colors | 3 | 0.45
2780 | 6279875 | 2780 | Technic, Pin with Short Friction Ridges | 11 | 0 | Black | Solid Colors | 64 | 0.16
32009 | 6271156 | 32009 | Technic, Liftarm, Modified Bent Thick 1 x 11.5 Double | 86 | 71 | Light Bluish Gray | Solid Colors | 2 | 3.46
32073 | 4166139 | 32073 | Technic, Axle 5L | 1 | 15 | White | Solid Colors | 1 | 0.66
32073 | 4114740 | 32073 | Technic, Axle 5L | 11 | 0 | Black | Solid Colors | 1 | 0.66
4265c | 6271165 | 4265c | Technic Bush 1/2 Smooth | 86 | 71 | Light Bluish Gray | Solid Colors | 2 | 0.1
44 | 4614799 | 44 | Technic, Axle and Pin Connector Toggle Joint Smooth | 5 | 4 | Red | Solid Colors | 1 | 0.25
32140 | 6271824 | 32140 | Technic, Liftarm, Modified Bent Thick L-Shape 2 x 4 | 1 | 15 | White | Solid Colors | 3 | 1.43
32140 | 6271831 | 32140 | Technic, Liftarm, Modified Bent Thick L-Shape 2 x 4 | 86 | 71 | Light Bluish Gray | Solid Colors | 2 | 1.43
32184 | 6276951 | 32184 | Technic, Axle and Pin Connector Perpendicular 3L with Center Pin Hole | 11 | 0 | Black | Solid Colors | 4 | 0.64
32269 | 6346517 | 32269 | Technic, Gear 20 Tooth Double Bevel | 2 | 19 | Tan | Solid Colors | 4 | 1.4
32270 | 32270194 | 32270 | Technic, Gear 12 Tooth Double Bevel | 86 | 71 | Light Bluish Gray | Solid Colors | 4 | 0.58
32278 | 4542578 | 32278 | Technic, Liftarm Thick 1 x 15 | 1 | 15 | White | Solid Colors | 3 | 4.0
32278 | 4542577 | 32278 | Technic, Liftarm Thick 1 x 15 | 86 | 71 | Light Bluish Gray | Solid Colors | 1 | 4.0
32316 | 4142135 | 32316 | Technic, Liftarm Thick 1 x 5 | 11 | 0 | Black | Solid Colors | 1 | 1.21
32316 | 4211651 | 32316 | Technic, Liftarm Thick 1 x 5 | 86 | 71 | Light Bluish Gray | Solid Colors | 3 | 1.21
32523 | 4142822 | 32523 | Technic, Liftarm Thick 1 x 3 | 11 | 0 | Black | Solid Colors | 3 | 0.7
32523 | 4208160 | 32523 | Technic, Liftarm Thick 1 x 3 | 1 | 15 | White | Solid Colors | 3 | 0.7
32523 | 4211655 | 32523 | Technic, Liftarm Thick 1 x 3 | 86 | 71 | Light Bluish Gray | Solid Colors | 1 | 0.7
32524 | 4495935 | 32524 | Technic, Liftarm Thick 1 x 7 | 11 | 0 | Black | Solid Colors | 1 | 1.74
32524 | 4495927 | 32524 | Technic, Liftarm Thick 1 x 7 | 1 | 15 | White | Solid Colors | 2 | 1.74
32524 | 4495930 | 32524 | Technic, Liftarm Thick 1 x 7 | 86 | 71 | Light Bluish Gray | Solid Colors | 3 | 1.74
32525 | 6028103 | 32525 | Technic, Liftarm Thick 1 x 11 | 1 | 15 | White | Solid Colors | 2 | 2.8
32526 | 4142823 | 32526 | Technic, Liftarm, Modified Bent Thick L-Shape 3 x 5 | 11 | 0 | Black | Solid Colors | 7 | 1.77
32526 | 4585040 | 32526 | Technic, Liftarm, Modified Bent Thick L-Shape 3 x 5 | 1 | 15 | White | Solid Colors | 1 | 1.77
3707 |  | 3707 | Technic, Axle 8L | 1 | 15 | White | Solid Colors | 2 | 1.18
3708 | 370826 | 3708 | Technic, Axle 12L | 11 | 0 | Black | Solid Colors | 11 | 1.83
3713 | 6275844 | 3713 | Technic Bush | 86 | 71 | Light Bluish Gray | Solid Colors | 13 | 0.14
37312c01 |  | 37312c01 | Electric Sensor, Force - SPIKE Prime | 11 | 0 | Black | Solid Colors | 2 | 18.81
3743 | 4211450 | 3743 | Technic, Gear Rack 1 x 4 | 86 | 71 | Light Bluish Gray | Solid Colors | 43 | 0.79
3749 | 4666579 | 3749 | Technic, Axle 1L with Pin without Friction Ridges | 2 | 19 | Tan | Solid Colors | 2 | 0.22
39367c02 | 6287602 | 39367c02 | Wheel 56 x 14 Technic with Axle Hole and 8 Pin Holes with Fixed Black Rubber Tire | 11 | 0 | Black | Solid Colors | 1 | 0
39790 | 6295161 | 39790 | Technic, Liftarm, Modified Frame Thick 11 x 15 Open Center | 11 | 0 | Black | Solid Colors | 1 | 0
41239 | 4522934 | 41239 | Technic, Liftarm Thick 1 x 13 | 86 | 71 | Light Bluish Gray | Solid Colors | 2 | 3.3
42003 | 6273712 | 42003 | Technic, Axle and Pin Connector Perpendicular 3L with 2 Pin Holes | 5 | 4 | Red | Solid Colors | 2 | 0.77
42003 | 6273708 | 42003 | Technic, Axle and Pin Connector Perpendicular 3L with 2 Pin Holes | 11 | 0 | Black | Solid Colors | 2 | 0.77
43093 | 4206482 | 43093 | Technic, Axle 1L with Pin with Friction Ridges | 7 | 1 | Blue | Solid Colors | 8 | 0.26
44294 | 4211805 | 44294 | Technic, Axle 7L | 86 | 71 | Light Bluish Gray | Solid Colors | 2 | 1.05
4519 |  | 4519 | Technic, Axle 3L | 1 | 15 | White | Solid Colors | 1 | 0.43
48989 | 6282158 | 48989 | Technic, Pin Connector Perpendicular 3L with 4 Pins | 86 | 71 | Light Bluish Gray | Solid Colors | 9 | 1.22
54696c01 |  | 54696c01 | Electric, Motor SPIKE Prime, Medium Angular | 86 | 71 | Light Bluish Gray | Solid Colors | 5 | 49.53
56903 | 6013484 | 56903 | Wheel 18mm D. x 8mm with Fake Bolts and Shallow Spokes and Axle Hole | 1 | 15 | White | Solid Colors | 1 | 1.0
6538c | 6212049 | 6538c | Technic, Axle Connector 2L (Smooth with x Hole + Orientation) | 1 | 15 | White | Solid Colors | 7 | 0.4
60479 | 4514842 | 60479 | Plate 1 x 12 | 1 | 15 | White | Solid Colors | 1 | 1.95
60484 |  | 60484 | Technic, Liftarm, Modified T-Shape Thick 3 x 3 | 1 | 15 | White | Solid Colors | 1 | 1.19
60485 | 6130010 | 60485 | Technic, Axle 9L | 3 | 14 | Yellow | Solid Colors | 2 | 1.3
63869 | 6331441 | 63869 | Technic, Axle and Pin Connector Perpendicular Triple | 86 | 71 | Light Bluish Gray | Solid Colors | 2 | 1.05
64178 | 4540797 | 64178 | Technic, Liftarm, Modified Frame Thick 5 x 11 Open Center | 86 | 71 | Light Bluish Gray | Solid Colors | 1 | 7.0
64179 | 4539880 | 64179 | Technic, Liftarm, Modified Frame Thick 5 x 7 Open Center | 86 | 71 | Light Bluish Gray | Solid Colors | 4 | 5.3
64179 | 6016154 | 64179 | Technic, Liftarm, Modified Frame Thick 5 x 7 Open Center | 11 | 0 | Black | Solid Colors | 1 | 5.3
64781 | 6302830 | 64781 | Technic, Gear Rack 1 x 13 with Axle and Pin Holes | 11 | 0 | Black | Solid Colors | 2 | 3.13
6536 | 6261373 | 6536 | Technic, Axle and Pin Connector Perpendicular | 5 | 4 | Red | Solid Colors | 1 | 0.39
6558 | 6299413 | 6558 | Technic, Pin 3L with Friction Ridges | 7 | 1 | Blue | Solid Colors | 30 | 0.31
87082 | 6321303 | 87082 | Technic, Pin 3L with Friction Ridges and Center Pin Hole | 86 | 71 | Light Bluish Gray | Solid Colors | 2 | 0.5
94925 | 4640536 | 94925 | Technic, Gear 16 Tooth (Second Version - Reinforced) | 86 | 71 | Light Bluish Gray | Solid Colors | 12 | 0.7
Total qty | Total Weight
298 | 535.22

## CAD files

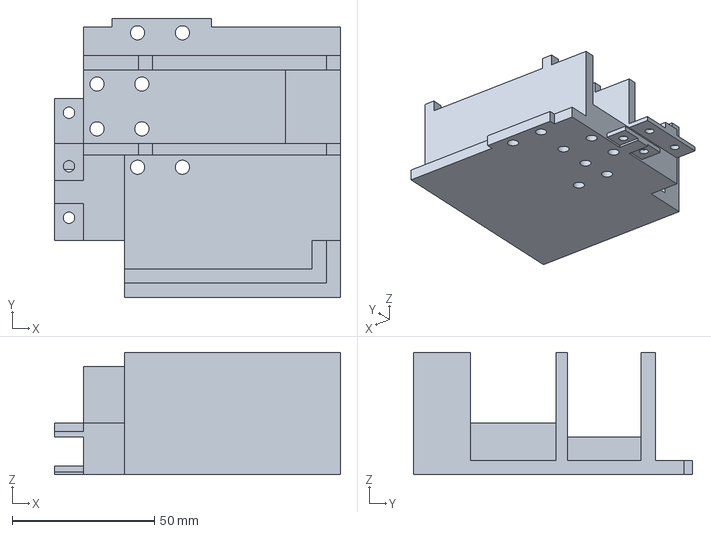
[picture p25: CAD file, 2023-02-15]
Construction/3D Printing/Printable Files/Side Assembly/Side Assembly.3mf
100.5 x 98.0 x 43.0 mm

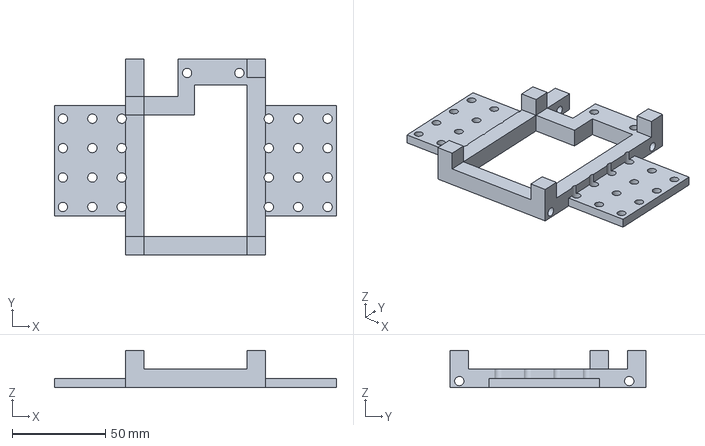
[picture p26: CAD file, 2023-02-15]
Construction/3D Printing/Printable Files/Trolley Base/Trolley Base Assembly.3mf
151.0 x 105.0 x 20.0 mm

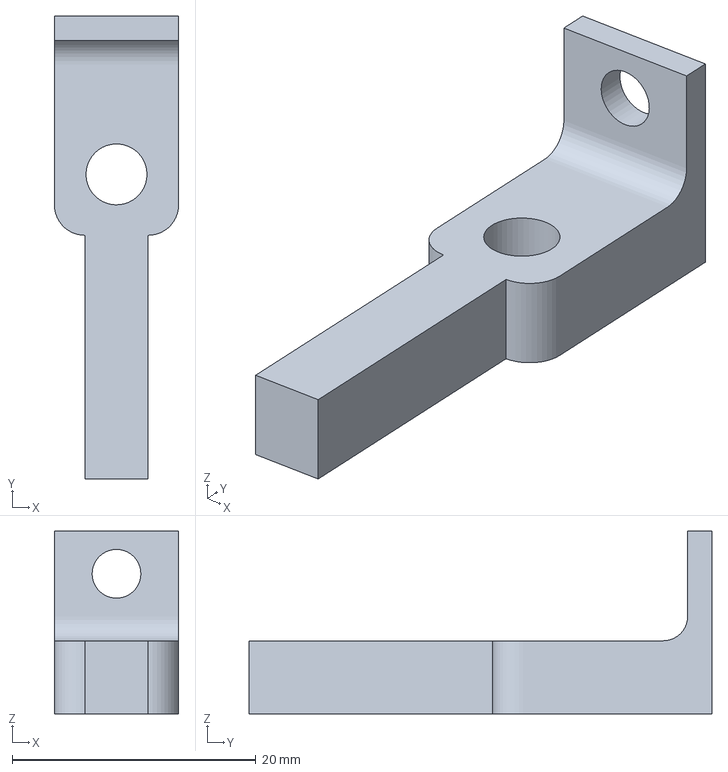
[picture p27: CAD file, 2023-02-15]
Construction/3D Printing/Printable Files/End-Axle Supports/End-Axle Supports.3mf
10.2 x 38.0 x 15.0 mm

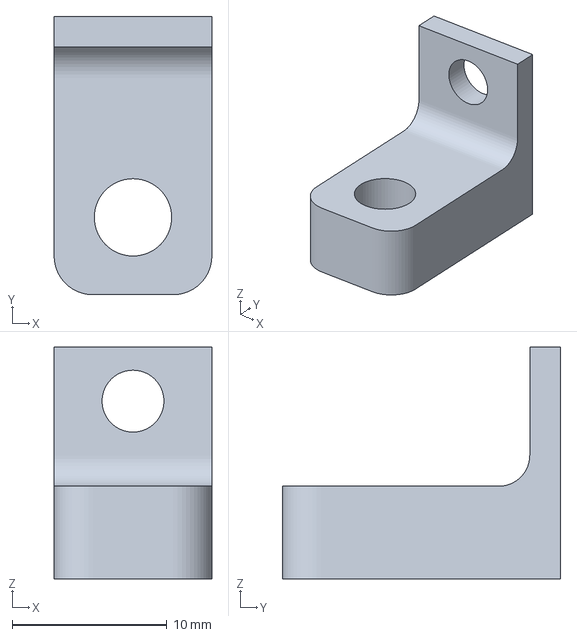
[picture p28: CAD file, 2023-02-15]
Construction/3D Printing/Printable Files/Force Sensor Holders/Force Sensor Holders.3mf
10.2 x 18.0 x 15.0 mm

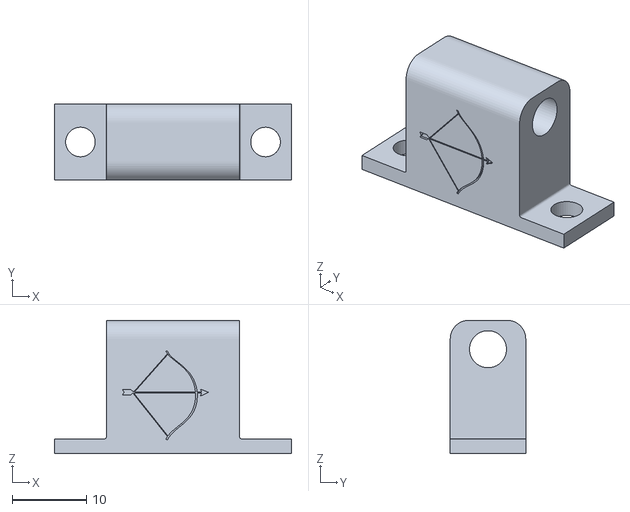
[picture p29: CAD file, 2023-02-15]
Construction/3D Printing/Printable Files/Mid-Axle Supports/Mid-Axle Supports.stl
32.0 x 10.2 x 18.0

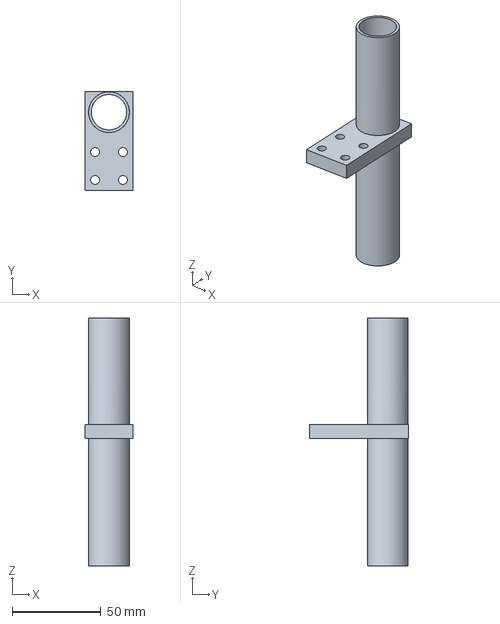
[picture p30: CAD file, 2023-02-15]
Construction/3D Printing/Printable Files/pH Sensor Guide Tube/pH Sensor Guide Tube.3mf
27.0 x 56.0 x 140.0 mm

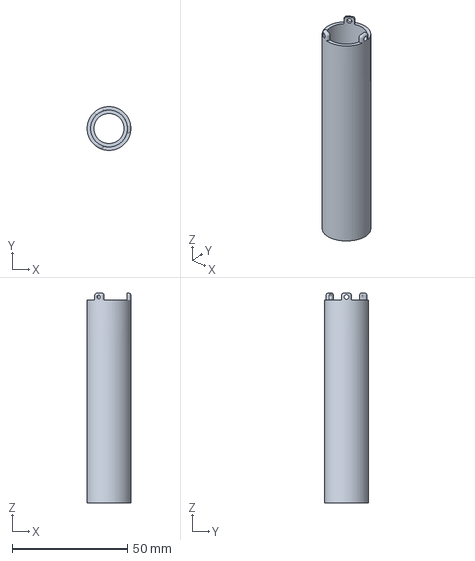
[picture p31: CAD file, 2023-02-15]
Construction/3D Printing/Printable Files/pH Sensor Sleeve/pH Sensor Sleeve.3mf
19.0 x 19.0 x 91.0 mm

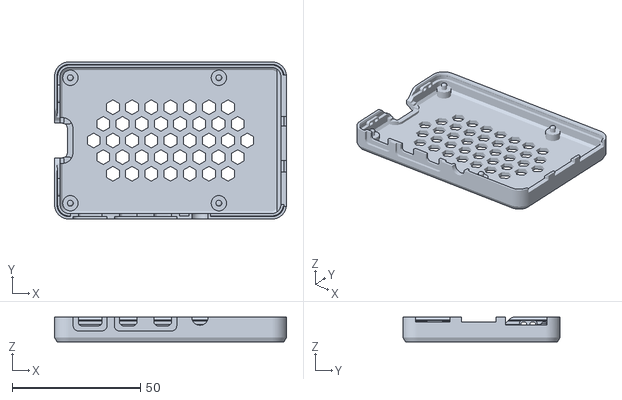
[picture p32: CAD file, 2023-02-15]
Construction/3D Printing/Printable Files/R-Pi Case/R-Pi Case.stl
90.6 x 61.4 x 9.70

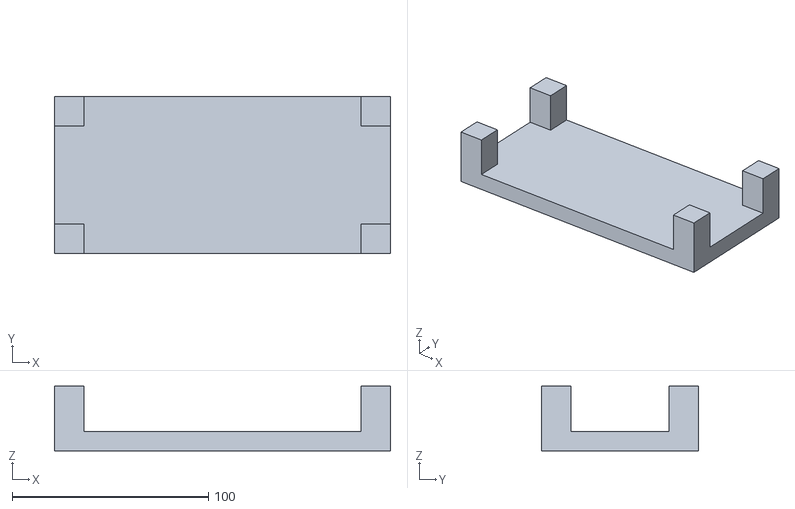
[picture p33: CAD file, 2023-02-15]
Construction/3D Printing/Printable Files/Reservoir Tanks and Stand/Reservoir Stand.stl
171.0 x 80.0 x 33.0

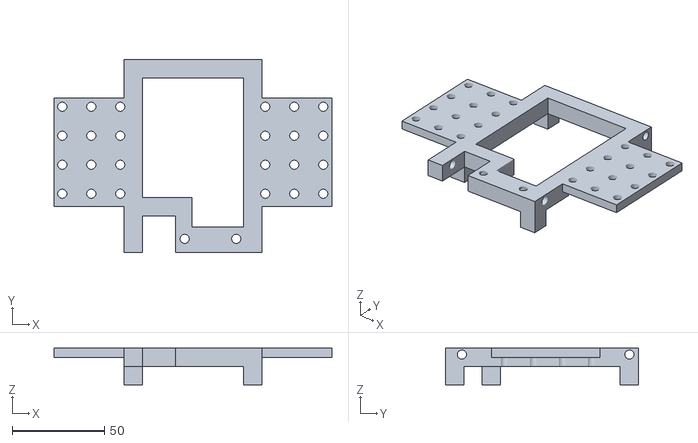
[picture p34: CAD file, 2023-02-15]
Construction/3D Printing/Printable Files/Trolley Base/Trolley Base.obj
151.0 x 105.0 x 20.0

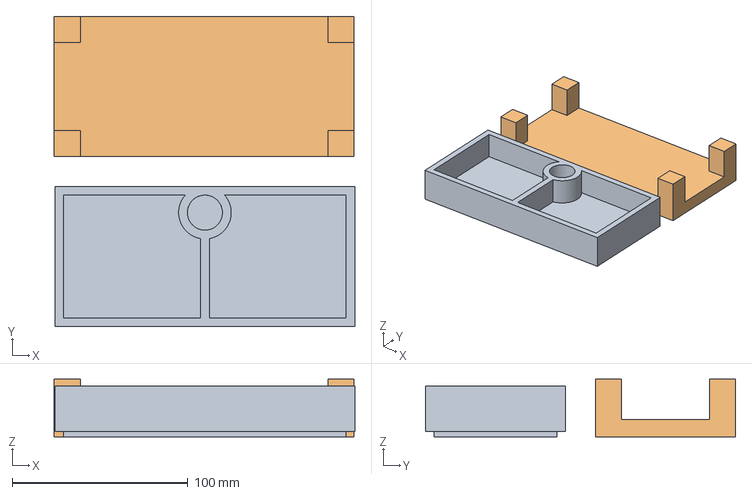
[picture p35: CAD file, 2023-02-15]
Construction/3D Printing/Printable Files/Reservoir Tanks and Stand/Reservoir Tanks and Stand.3mf
171.5 x 176.9 x 33.0 mm
Reservoir Tanks.stl
Reservoir Stand.stl

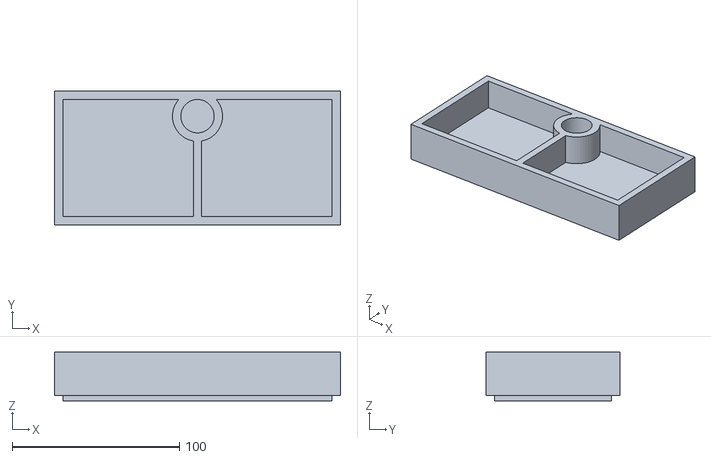
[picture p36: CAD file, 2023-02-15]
Construction/3D Printing/Printable Files/Reservoir Tanks and Stand/Reservoir Tanks.stl
171.0 x 80.0 x 29.0

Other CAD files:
Construction/3D Printing/Printable Files/End-Axle Supports/End-Axle Supports.f3d
Construction/3D Printing/Printable Files/End-Axle Supports/End-Axle Supports.obj
Construction/3D Printing/Printable Files/Mid-Axle Supports/Mid-Axle Supports.f3d
Construction/3D Printing/Printable Files/Mid-Axle Supports/Mid-Axle Supports.obj
Construction/3D Printing/Printable Files/Reservoir Tanks and Stand/Reservoir Stand.f3d
Construction/3D Printing/Printable Files/Reservoir Tanks and Stand/Reservoir Stand.obj
Construction/3D Printing/Printable Files/Reservoir Tanks and Stand/Reservoir Tanks.f3d
Construction/3D Printing/Printable Files/Reservoir Tanks and Stand/Reservoir Tanks.obj
Construction/3D Printing/Printable Files/Side Assembly/Side Assembly.f3d
Construction/3D Printing/Printable Files/Side Assembly/Side Assembly.obj
Construction/3D Printing/Printable Files/Trolley Base/Trolley Base Assembly.f3d
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

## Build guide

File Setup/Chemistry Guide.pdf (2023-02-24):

# LEGOLAS Chemistry Guide*

*For Henderson-Hasselbalch Experiment

- Glacial Acetic Acid (> 100 mL* recommended for multiple experiments)
- Sodium Acetate Anhydrous (> 80 g*)
- Deionized Water (5-10 L*)
- Extra pH storage solution (1 M KCl)
- Alternatively, you can make the solution, in which case you need KCl Salt (>10 g*)
- Chemistry Equipment
- Graduated Cylinder
- Paper or Plastic Funnel (for pouring salts into mixing containers)
- Digital Scale (mg accuracy)
- 1 mL Syringes
- 50 – 400 mL glassware with screw on/off tops (for holding solutions)

## Items Needed

*recommended for ~2 L of both acid and base (20 reservoirs full)

## 1. Solution Preparation Guide

Solution | DI Water Volume | Active Chemical Amount | Tips
[1M] Acetic Aid | 50 mL | 3 mL Glacial Acetic Acid | Use syringe (acid) and graduated cylinder (water). Mix well in container and keep lid shut until time of experiment.
[1M] Acetate Base | 50 mL | 4300 mg Sodium Acetate Anhydrous | Use mg scale and graduated cylinder. Mix well in container and keep lid shut until time of experiment. Do not transfer base to reservoirs via syringe.
[1M] KCl (pH Storage) | 50 mL | 3727 mg KCl Salt | Use mg scale and graduated cylinder. Mix well in container and use to refill pH storage caps when needed.

This is a guide for creating ~50 mL of each solution. The amounts can be scaled up for larger batches.

## 2. Setting up the Sample Space

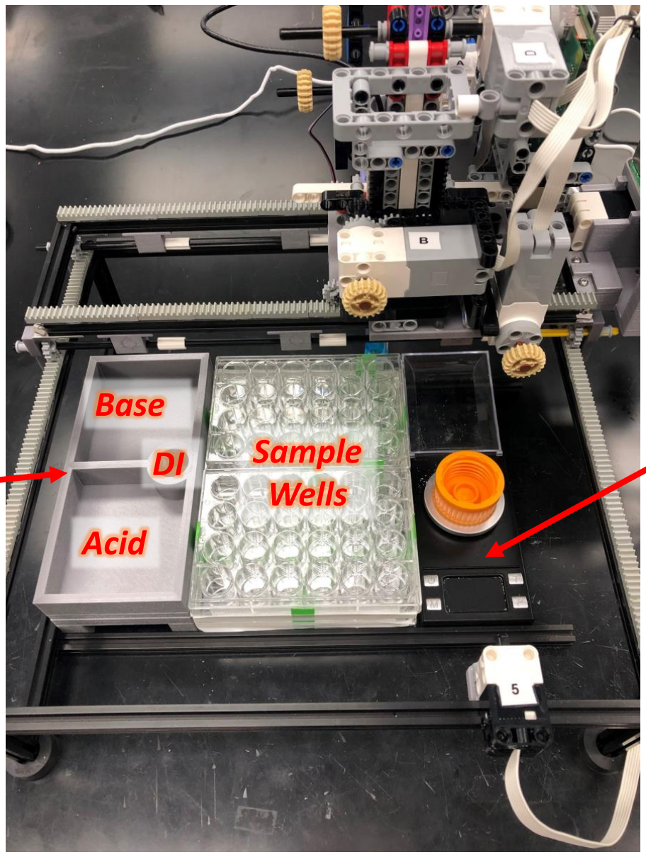
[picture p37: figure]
Acid; Base; Sample; Wells

Reservoir

Calibration
Scale

Manually move the trolley and bridge so that

the pH sensor is out of the sample space area.

Slide the Reservoir Stand and Tanks in

between the sample space guide extrusions,

adjusting their width if necessary to keep the

reservoir tightly clamped and stationary.

Next, slide the sample wells in as shown, and

lastly place the scale. This scale will be used

to calibrate the volume the syringe is able to

pick up using the LEGO motor controls.

## 3. Implementation Tips

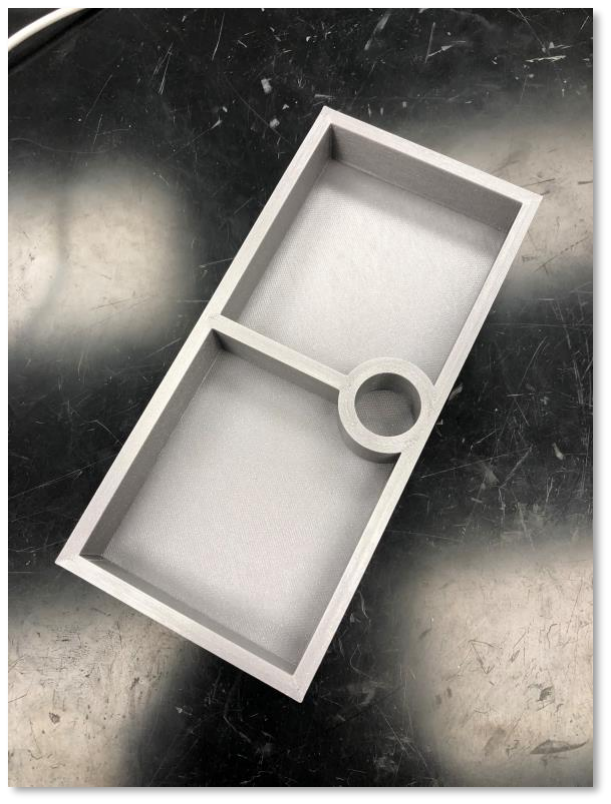
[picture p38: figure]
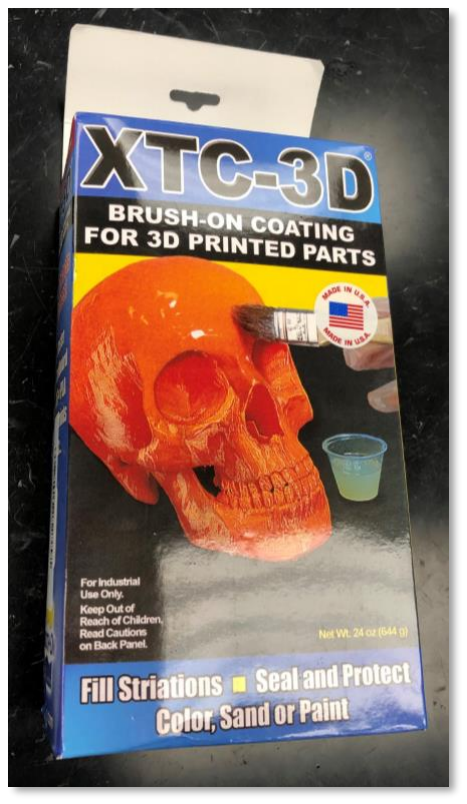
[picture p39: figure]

Each Reservoir Tank (left) holds 50 mL of either Acid /

Base solution when completely full. To avoid changes in

pH due to exposure to air, experimental solutions should

only be dispensed into the reservoir tanks immediately

prior to the execution of an autonomous loop. Do not

use a syringe to dispense the liquids from their containers

into the reservoirs. These reservoirs can be refilled

during an experiment if necessary (they hold enough to

create 50 2 mL samples). It is also recommended to use

an epoxy coating (right) on the inside of the reservoir

tanks, where they contact the solution. This prevents any

absorbance of the solution by the PLA since it is prone to

swelling and allowing leaks between FDM layer lines

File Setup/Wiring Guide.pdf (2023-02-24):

# LEGOLAS Wiring Guide

- (2x) BuildHAT chargers
- (1x) LEGO Inventor Motor Extension Cable
- (1x) BNC connector cable (comes with Arduino pH sensor)
- (3x) 2-3” Jumper Wires (Arduino Breadboard Compatible)
- Preferably a Red, Black, and Blue Wire
- (1x) USB 2.0 Printer Cable - A-Male to B-Male Cord (Will need > 18” cord length)
- (1x) Laboratory Retort Support Stand with Rings (Chemistry Ring Stand)
- Need >18” height, at least one ring attachment, and a clamp attachment (see step 1)
- (optional) An adjustable wrench for tightly securing the retort stand nut (see step 1)

## Items Needed

## 1. Build the Ring Stand

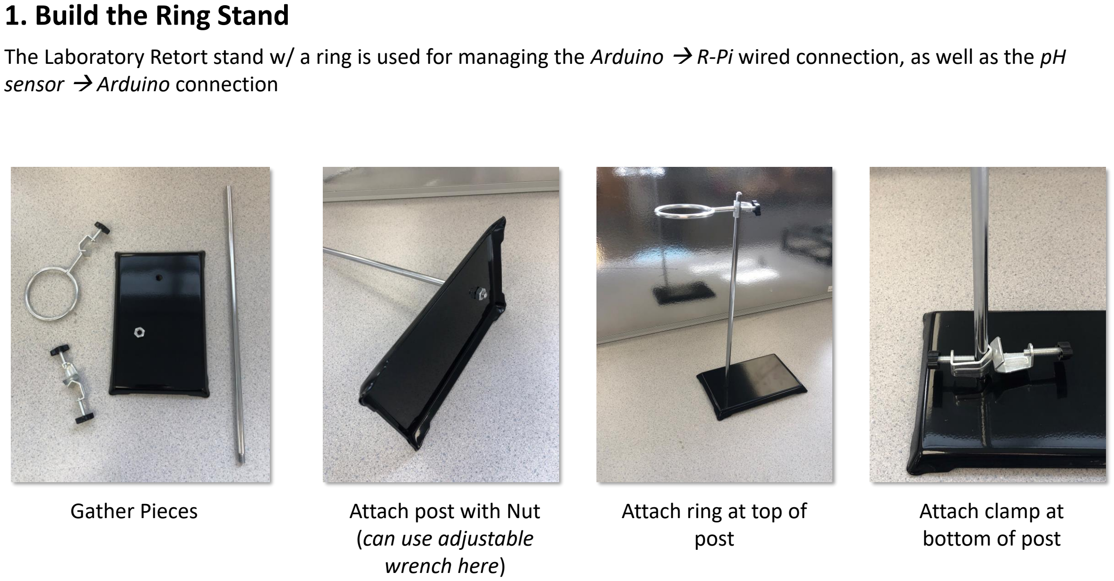
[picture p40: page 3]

The Laboratory Retort stand w/ a ring is used for managing the Arduino → R-Pi wired connection, as well as the pH sensor → Arduino connection

Gather Pieces | Attach post with Nut (can use adjustable wrench here)

Attach ring at top of
post

Attach clamp at
bottom of post

## 2. Wire Arduino Connections

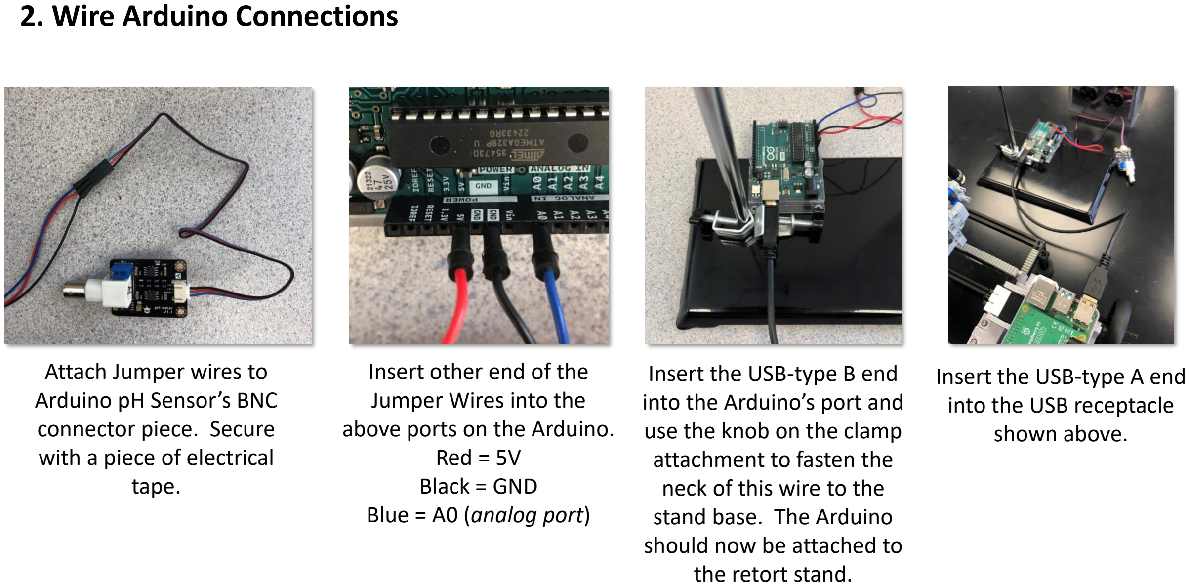
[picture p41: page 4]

Attach Jumper wires to
Arduino pH Sensor’s BNC
connector piece. Secure
with a piece of electrical tape.

Insert other end of the
Jumper Wires into the
above ports on the Arduino. Red = 5V
Black = GND
Blue = A0 (analog port)

Insert the USB-type B end
into the Arduino’s port and use the knob on the clamp
attachment to fasten the
neck of this wire to the
stand base. The Arduino
should now be attached to
the retort stand.

Insert the USB-type A end
into the USB receptacle
shown above.

## 3. Connect pH Sensor

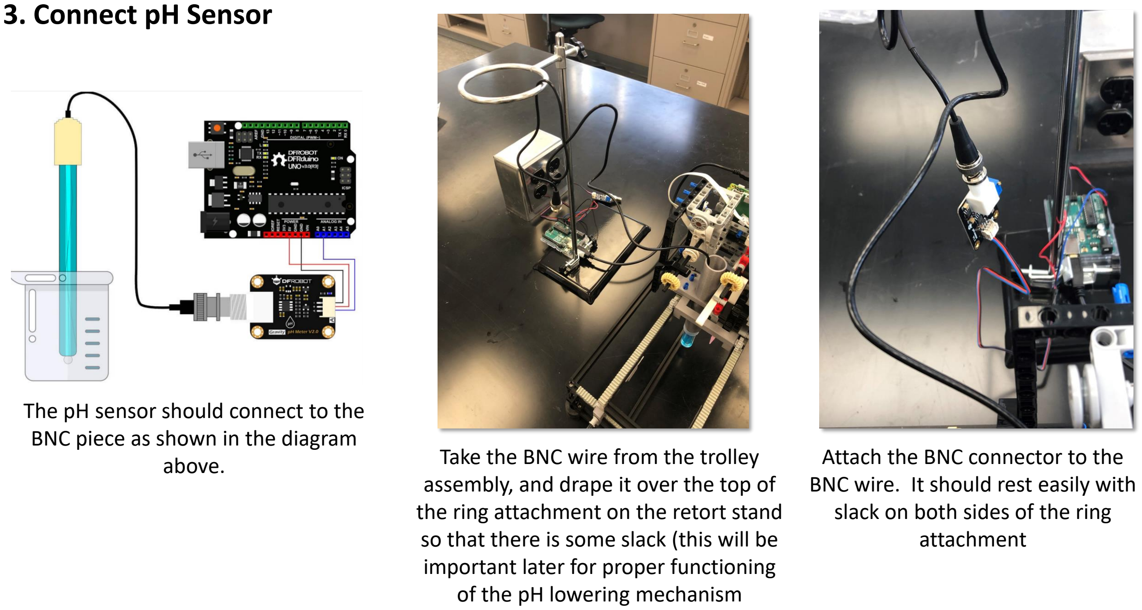
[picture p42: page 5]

The pH sensor should connect to the BNC piece as shown in the diagram
above. | Take the BNC wire from the trolley
| assembly, and drape it over the top of
| the ring attachment on the retort stand
| so that there is some slack (this will be
| important later for proper functioning
| of the pH lowering mechanism

Attach the BNC connector to the BNC wire. It should rest easily with slack on both sides of the ring attachment

## 4. Wire the Side Assembly R-Pi + BH Stack (#A)

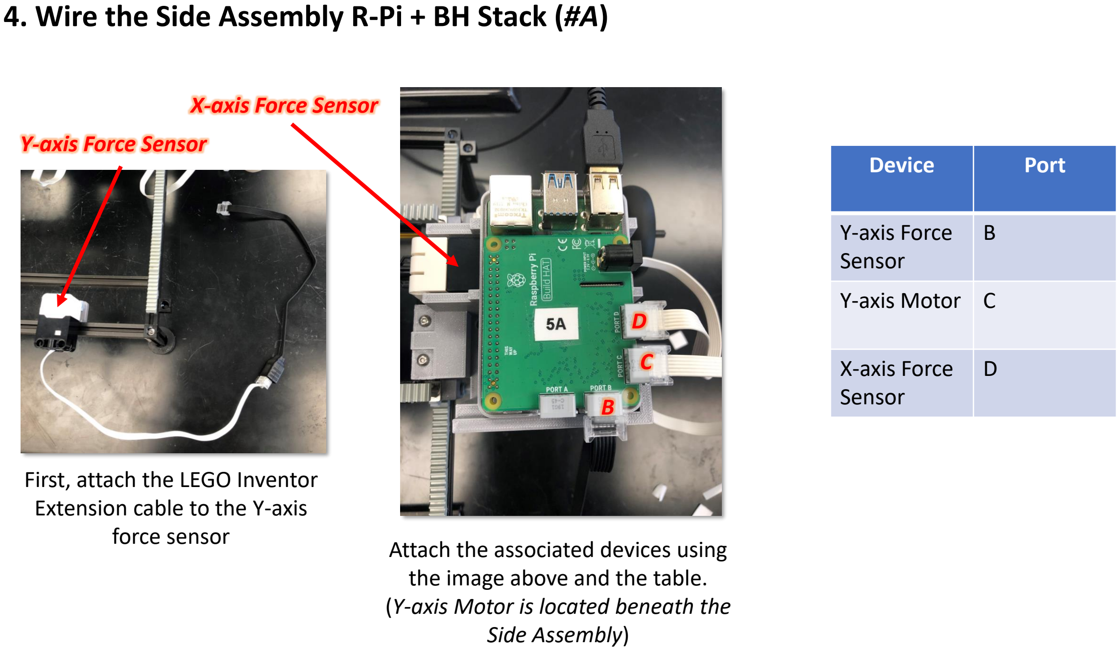
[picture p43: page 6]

Device | Port
Y-axis Force Sensor | B
Y-axis Motor | C
X-axis Force Sensor | D

First, attach the LEGO Inventor Extension cable to the Y-axis
force sensor | Attach the associated devices using
| the image above and the table.
| (Y-axis Motor is located beneath the
| Side Assembly)

Y-axis Force Sensor

B

C

D

X-axis Force Sensor

## 5. Wire the Trolley R-Pi + BH Stack (#B)

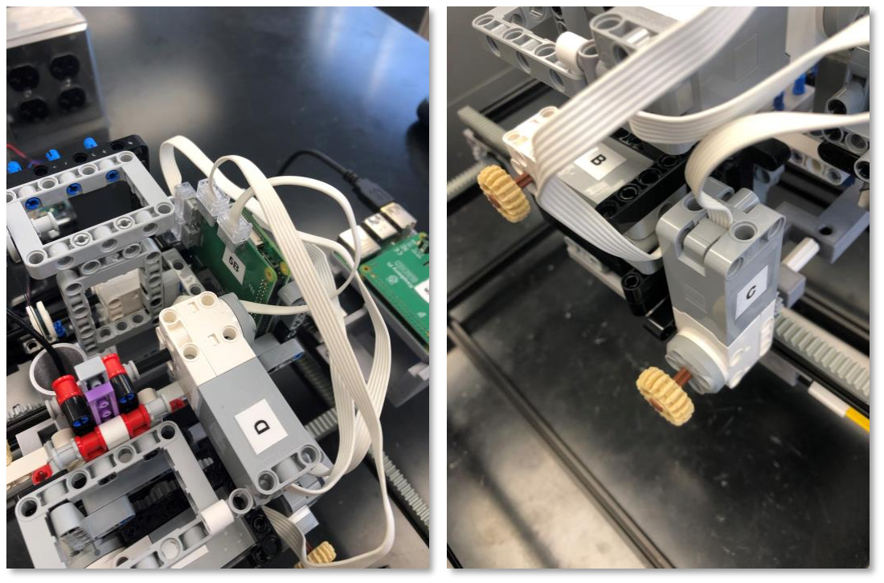
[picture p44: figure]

Attach the devices again,
this time for the trolley
motors and R-Pi + BH
Device | Port
Syringe Z-Motor | B
Syringe Plunger Motor | D
pH Sensor Z-Motor | A
X-axis Motor | C

It may be a good idea to
label the motors with
their port if you need to
unplug them later.

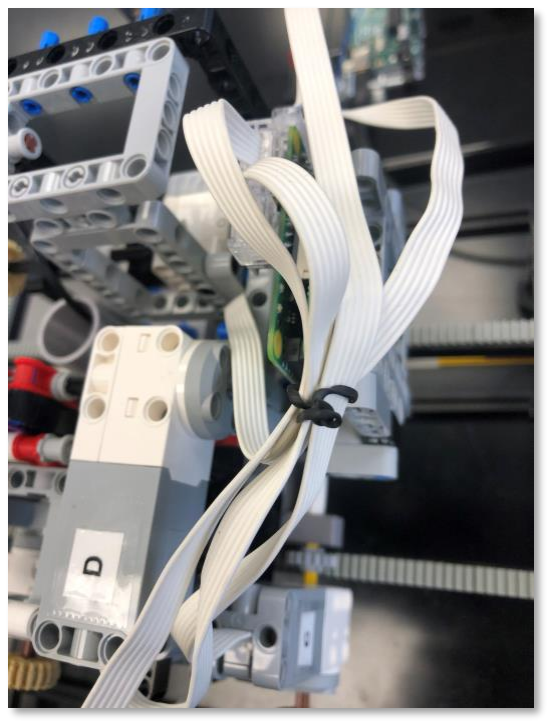
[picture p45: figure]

It is also recommended to
use a wire tie to keep the group of wires together in a more organized manner.

## 7. Connecting Power

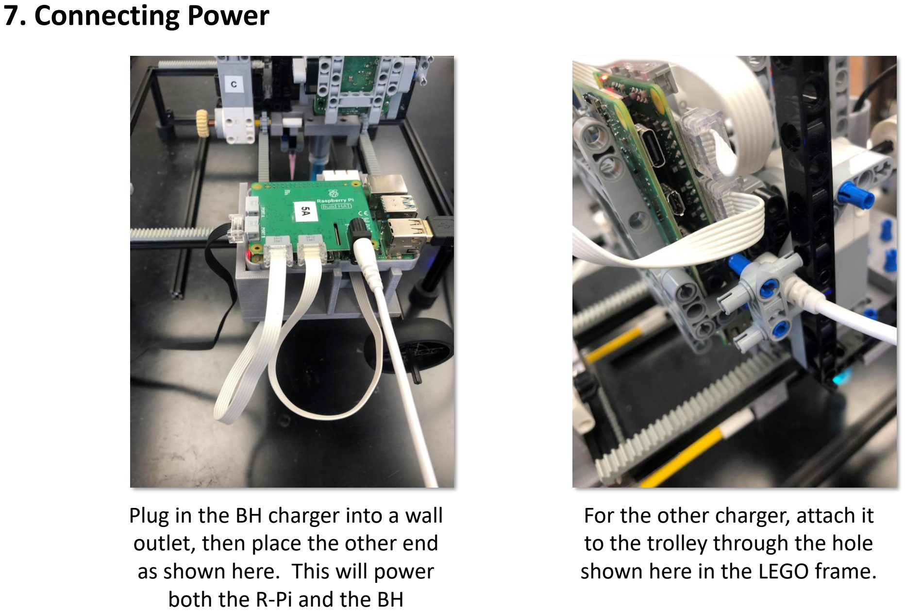
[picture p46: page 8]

Plug in the BH charger into a wall outlet, then place the other end as shown here. This will power both the R-Pi and the BH

For the other charger, attach it to the trolley through the hole shown here in the LEGO frame.

## 7. Wire Management Tips and Checks

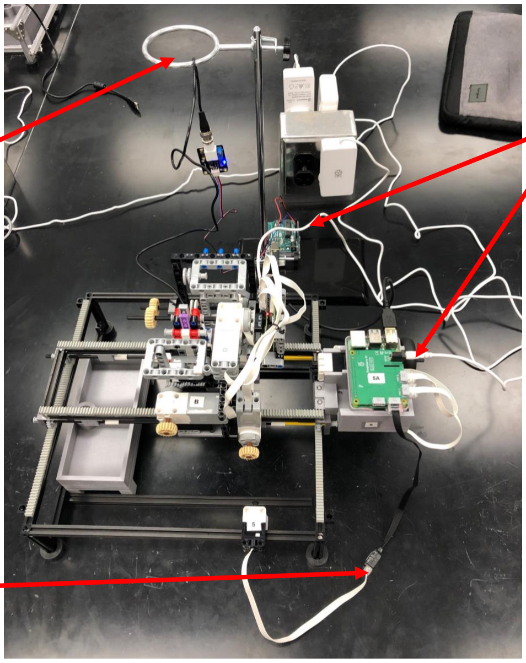
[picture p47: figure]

Once the wires are arranged, ensure you have enough slack in the BNC cord to allow the range of motion shown in this video. (https://youtube.com/shorts/R666TJzq6_A?feature=share) Repeat this process at all 4 corners of the cartesian space

Keep BH
charger cords
outside the
sample space,
with some
slack

Keep the
retort stand
around 3-6”
behind the
stand frame.

Keep Y-axis
force sensor
cord outside
the frame
space

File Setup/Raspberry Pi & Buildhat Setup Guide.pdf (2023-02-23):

# LEGOLAS Raspberry Pi & Buildhat Setup Guide

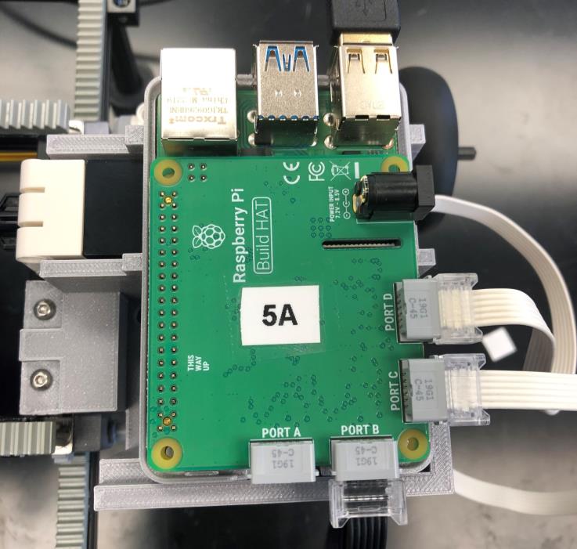
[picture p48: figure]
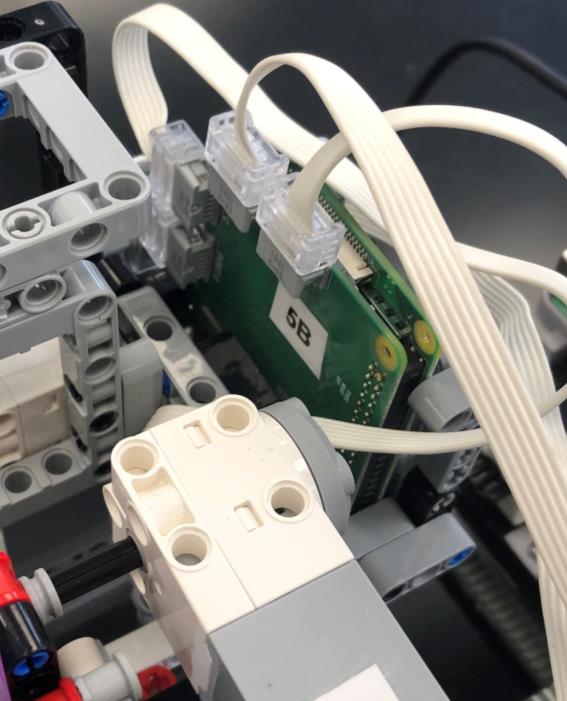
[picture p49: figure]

You will have two Raspberry Pi + Buildhat stacks, one which is located on the side assembly of the bridge (#A), and another which is located on the trolley (#B). Each contains a microSD card. The following steps may be applied to both microSD cards to prepare the R-Pi + BH for use in LEGOLAS. However, if you have a USB microSD Card Reader, you may also just follow the steps for one of the R-Pi + BH microSD cards, and then use the “SD card copying” accessory to copy the setup to the other microSD card (see Step 8)

- (1x) USB MicroSD Card Reader (optional)
- (1x) Monitor
- HDMI Input: You will need an HDMI → microUSB cable
- VGA Input: You will need a VGA → HDMI & a HDMI → microUSB
- (1x) Keyboard (USB Input)
- (1x) Mouse (USB Input)
- (1x) Buildhat Charger
- (2x) R-Pi + BH w/ microSD stacks
- (1x) WiFi Router (TP Link used in this example)
- (1x) Ethernet → Ethernet Cable

## Items Needed

You can Also Follow tips here to help Supplement this Guide
- BuildHAT Installation: https://www.raspberrypi.com/documentation/accessories/build-hat.html
- BuildHAT Documentation: https://buildhat.readthedocs.io/en/latest/buildhat/index.html
- BuildHAT Website: https://www.raspberrypi.com/products/build-hat/

## 1. Wiring

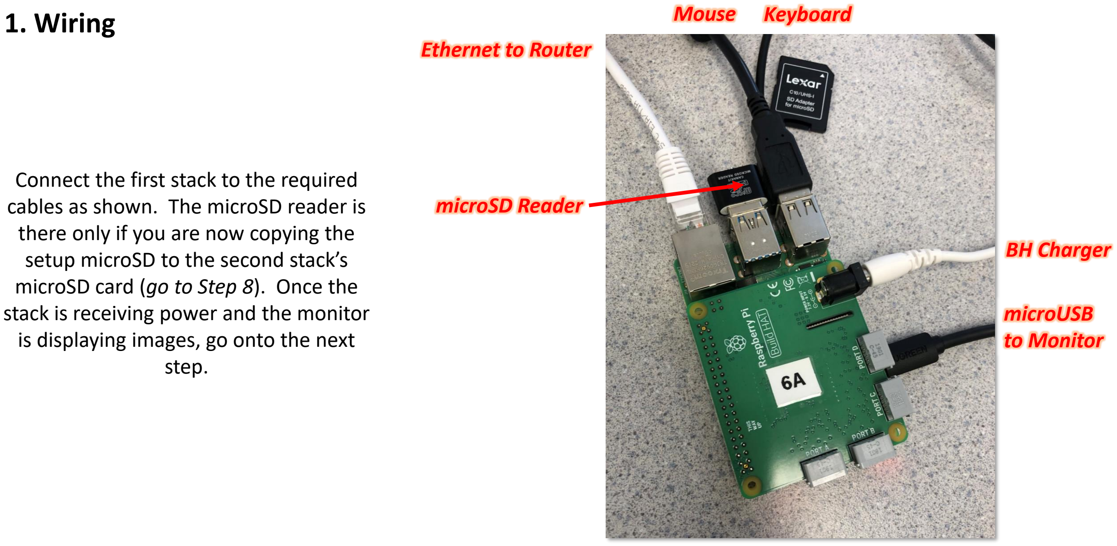
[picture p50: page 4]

Ethernet to Router

microSD Reader

BH Charger

microUSB
to Monitor

Mouse Keyboard

Connect the first stack to the required cables as shown. The microSD reader is there only if you are now copying the setup microSD to the second stack’s microSD card (go to Step 8). Once the stack is receiving power and the monitor is displaying images, go onto the next step.

## 2. Install R-Pi Operating System & Connecting to WiFi

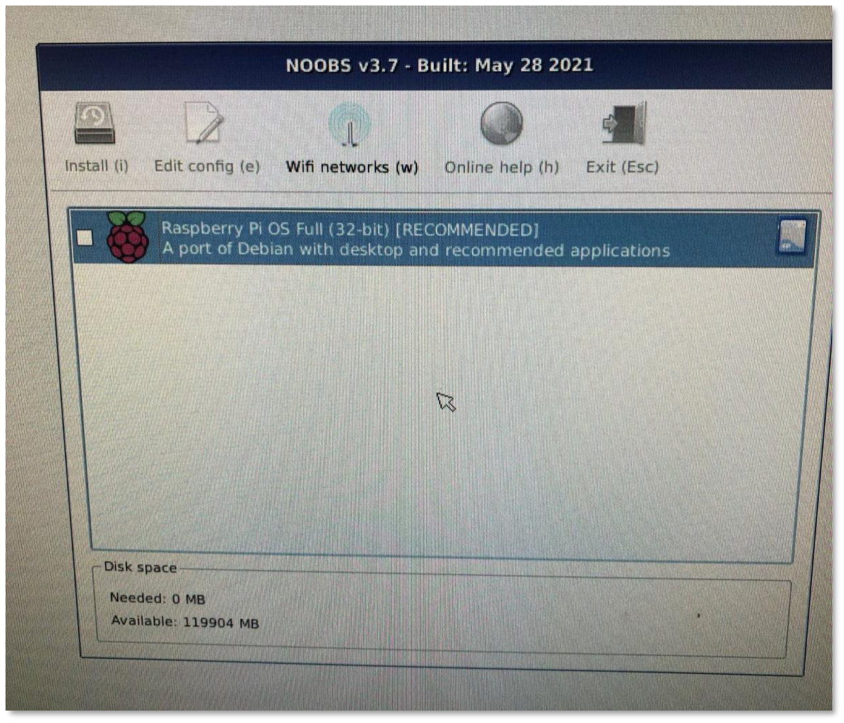
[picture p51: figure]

If the R-Pi was purchased with an SD card, it will likely have the Operating System downloaded. If not, follow the documentation to ensure it is downloaded (https://www.raspberrypi.com/documentation/computers/getting-started.html) on your compatible microSD card. Once plugged in, it will display this screen on the monitor. Select the R-Pi OS and click “Install.” This will likely take around 15-20 minutes to complete.

After the OS is installed, ensure you have your local WiFi router set up, and connect via password to your network. You may need to have the ethernet cable connecting the raspberry-pi to the router physically.

## 3. Configure and Assign a Hostname to R-Pi

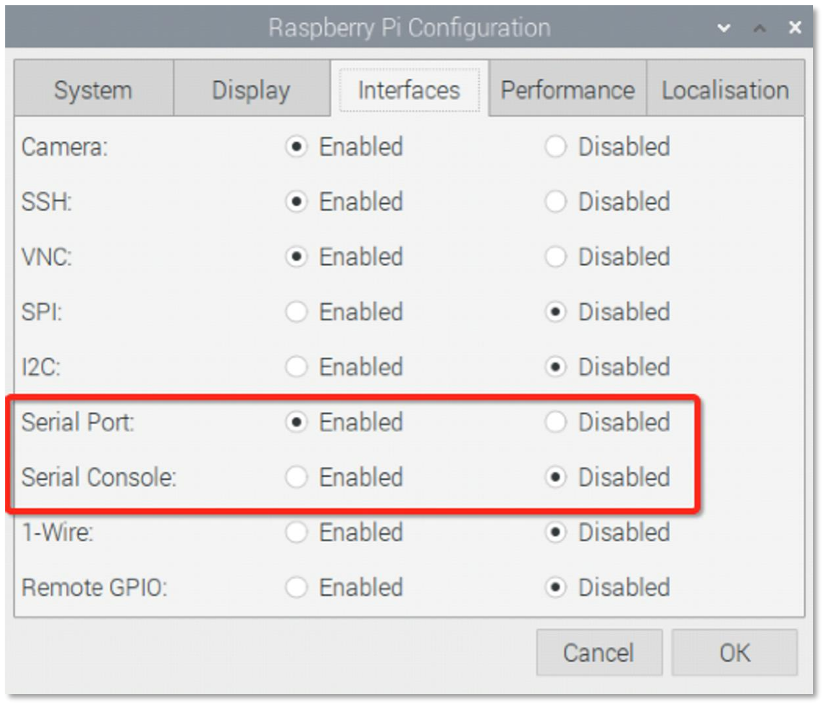
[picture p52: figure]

Once at the R-Pi Home Screen, select Preferences → Raspberry Pi Configuration from the dropdown and go to the Interfaces tab. Change the setup so that it matches the picture to the right, taking care to disable the Serial Console option as well. Press OK and choose not to reboot. Go to the System tab within the Configuration tab and rename your Raspberry-Pi on the hostname line (ex: raspberrypi5B). This is the name that will appear when you are reserving the address of your R-Pi on your local router. After renaming the R-Pi, reboot it.

## 4. Fix IP Address in Router

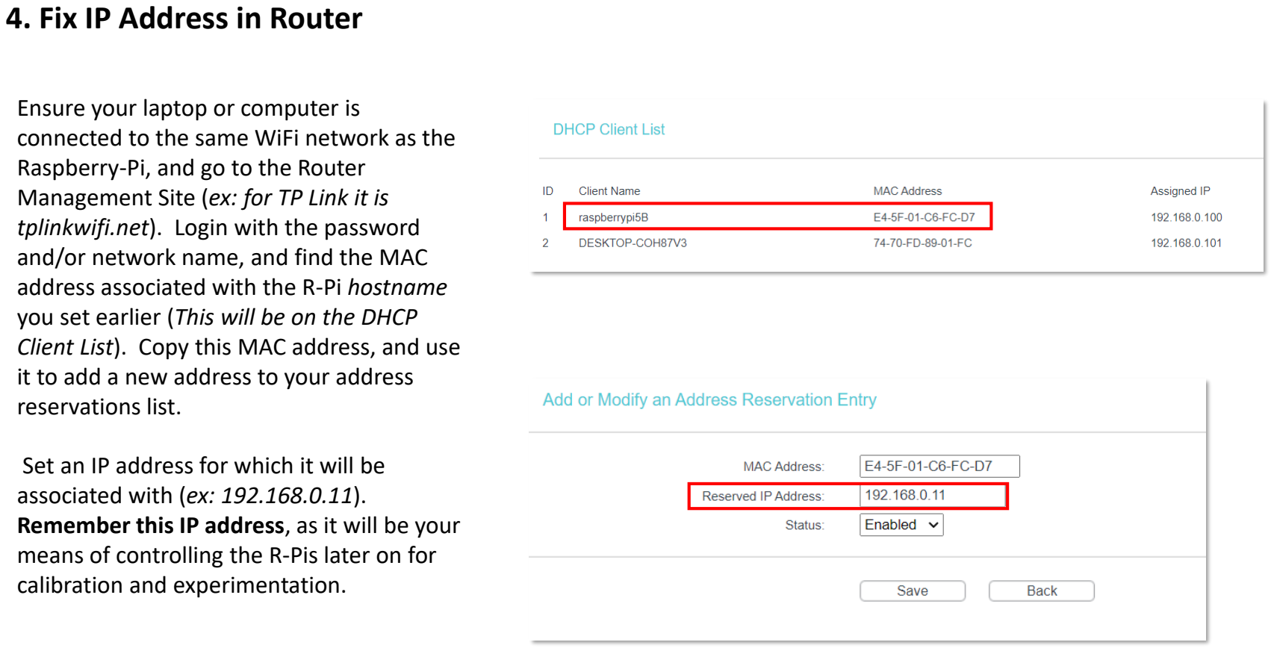
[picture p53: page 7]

Ensure your laptop or computer is connected to the same WiFi network as the Raspberry-Pi, and go to the Router Management Site (ex: for TP Link it is tplinkwifi.net). Login with the password and/or network name, and find the MAC address associated with the R-Pi hostname you set earlier (This will be on the DHCP Client List). Copy this MAC address, and use it to add a new address to your address reservations list.

Set an IP address for which it will be associated with (ex: 192.168.0.11). Remember this IP address, as it will be your means of controlling the R-Pis later on for calibration and experimentation.

## 5. Install Buildhat & RPyC Packages

We will need to install the BuildHAT
package so we can interface with the LEGO motors, and we must install the RPyC package so we can remotely control the R-Pi + BH stack.

If your local wifi router does not have internet access, connect instead to a network with internet access. Go back to the monitor in which you are interfacing with the R-Pi & type ctrl+alt+t
to open the command prompt. Enter the code to the right, line by line.

Commands

mkdir -p ~/git

cd ~/git

pip3 install buildhat

pip3 install rpyc

git clone https://github.com/tomerfiliba-org/rpyc.git

## 6. Setting up an Automatic RPyC Server

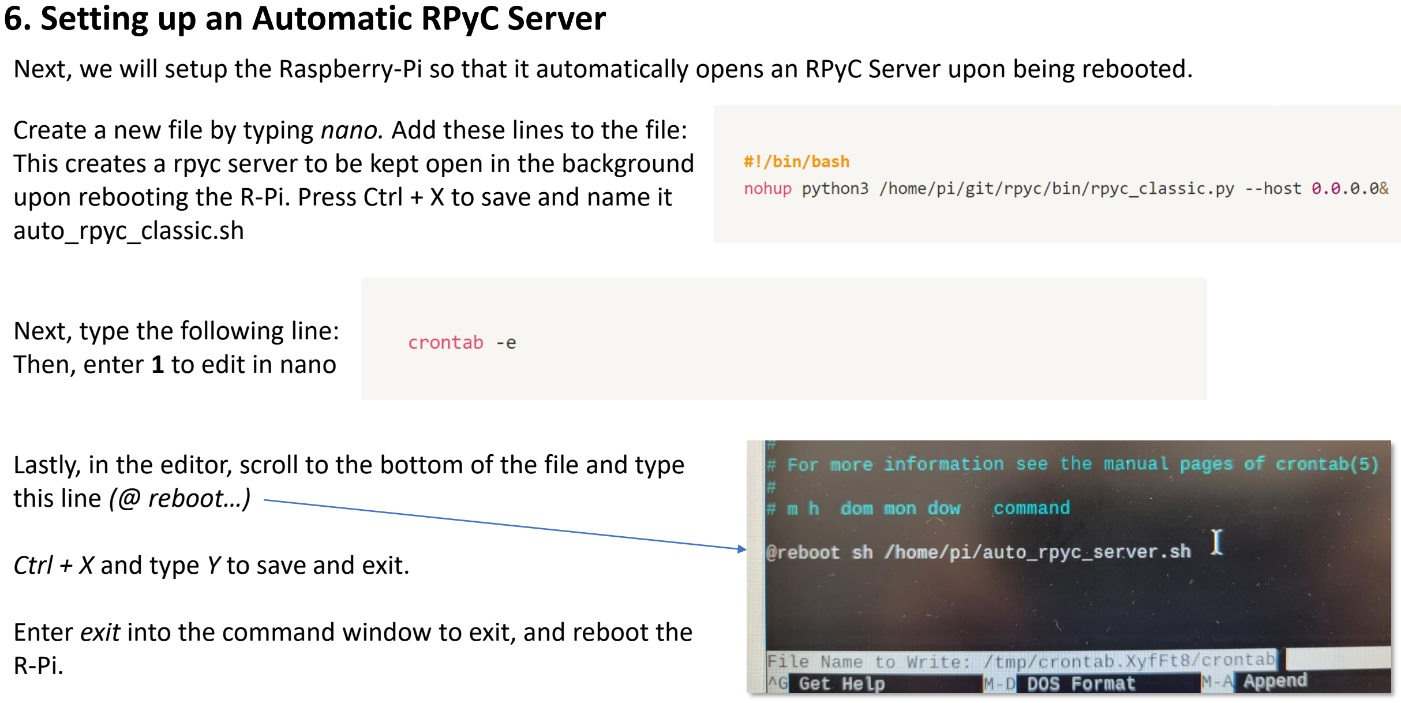
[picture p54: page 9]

Create a new file by typing nano. Add these lines to the file: This creates a rpyc server to be kept open in the background upon rebooting the R-Pi. Press Ctrl + X to save and name it auto_rpyc_classic.sh

Next, type the following line:
Then, enter 1 to edit in nano

Lastly, in the editor, scroll to the bottom of the file and type this line (@ reboot…)

Ctrl + X and type Y to save and exit.

Enter exit into the command window to exit, and reboot the R-Pi.

Next, we will setup the Raspberry-Pi so that it automatically opens an RPyC Server upon being rebooted.

## 7. Verify the Server is Working

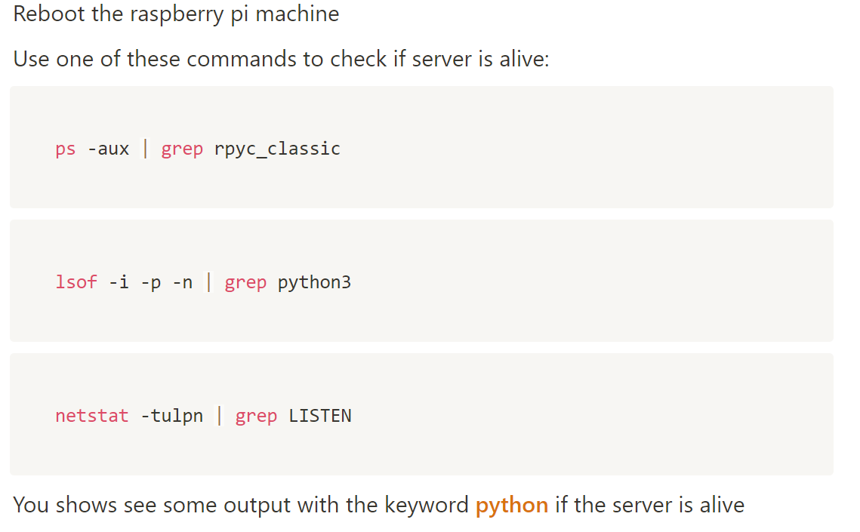
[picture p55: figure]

## 8. Copy to new SD Card (Optional)

Steps 1-7 may be repeated for the second R-Pi, or if you have access the USB microSD Reader, you can copy the microSD card you just setup to the new R-Pi’s microSD card.

Enter the new SD card into the USB reader and insert this into the R-Pi you just set up (see Step #1 for location), keeping the initial microSD card inserted into the R-Pi’s designated slot.

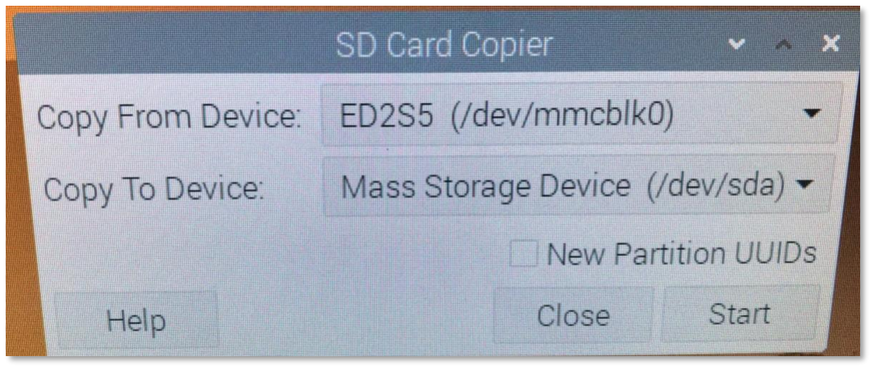
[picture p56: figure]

From the monitor, click on the dropdown and select Accessories → SD Card Copier and select the information shown in the image to the right. Confirm that you would like to overwrite the SD card and continue.

Once it is finished transferring, shutdown the R-Pi, remove the new microSD card from the USB reader, and insert into the new R-Pi stack. Then, hook this R-Pi up to your monitor, set a hostname for it (Step 3) and fix its address in your router (Step 4).

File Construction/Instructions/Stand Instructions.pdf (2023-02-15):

# LEGOLAS Stand Instructions

## Parts List

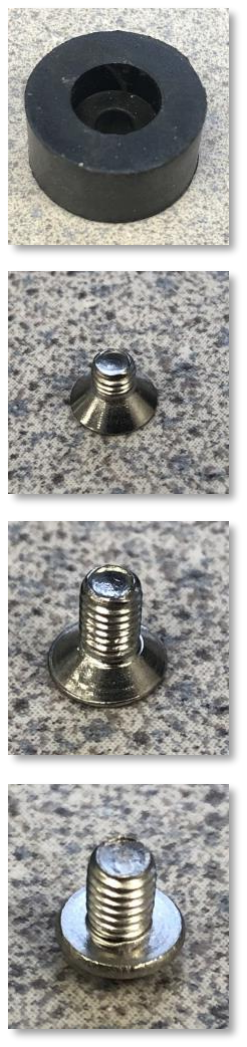
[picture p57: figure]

1”-Ø Rubber End Caps

M3 – 2mm Tapered Bolt*

M3 – 4mm Tapered Bolt*

M3 – 4mm Round-Head Bolt*

M3 – T-Slot Nut*

10 x 10 mm Profile – 75 mm Anodized Aluminum T-slot
Extrusion*

10 x 10 mm Profile –300 mm Anodized Aluminum T-slot
Extrusion*

M3 – Corner Cube*

*MakerBeam Product
- You will also need a 2 mm Hex bit
- Rubber End Caps may be replaced by MakerBeam 3D Printed End Caps
(https://www.makerbeam.com/makerbeam-3d-printed-end-caps-for-makerbeam-4p.html)

## 4 x

## 10 x

## 14 x

## 2 x

## 12 x

## 12 x

## 4 x

## 7 x

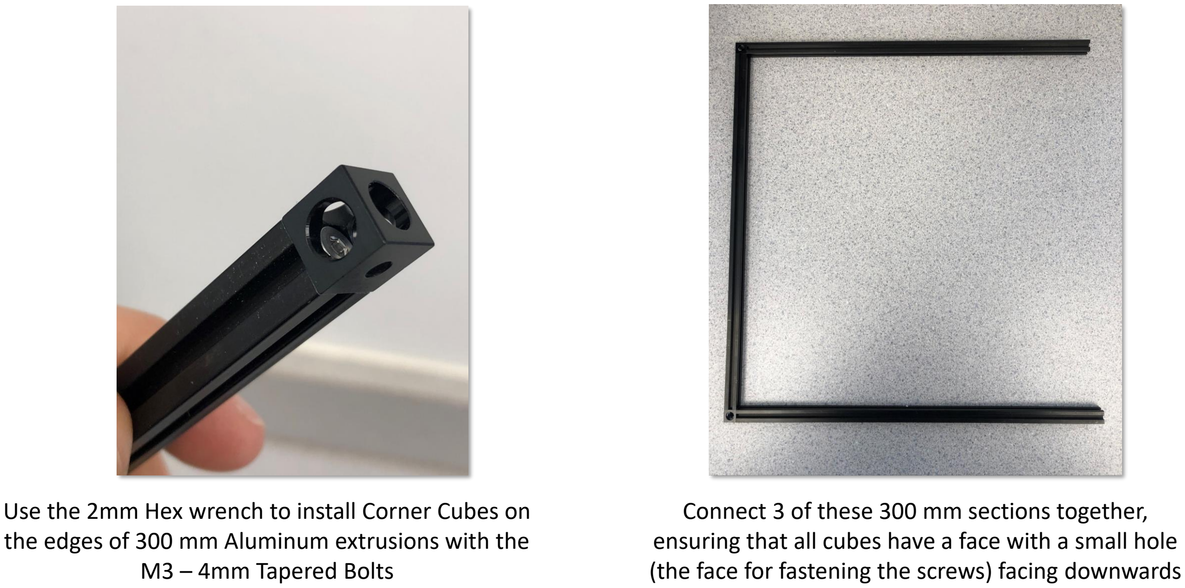
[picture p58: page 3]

Use the 2mm Hex wrench to install Corner Cubes on the edges of 300 mm Aluminum extrusions with the M3 – 4mm Tapered Bolts

Connect 3 of these 300 mm sections together, ensuring that all cubes have a face with a small hole (the face for fastening the screws) facing downwards

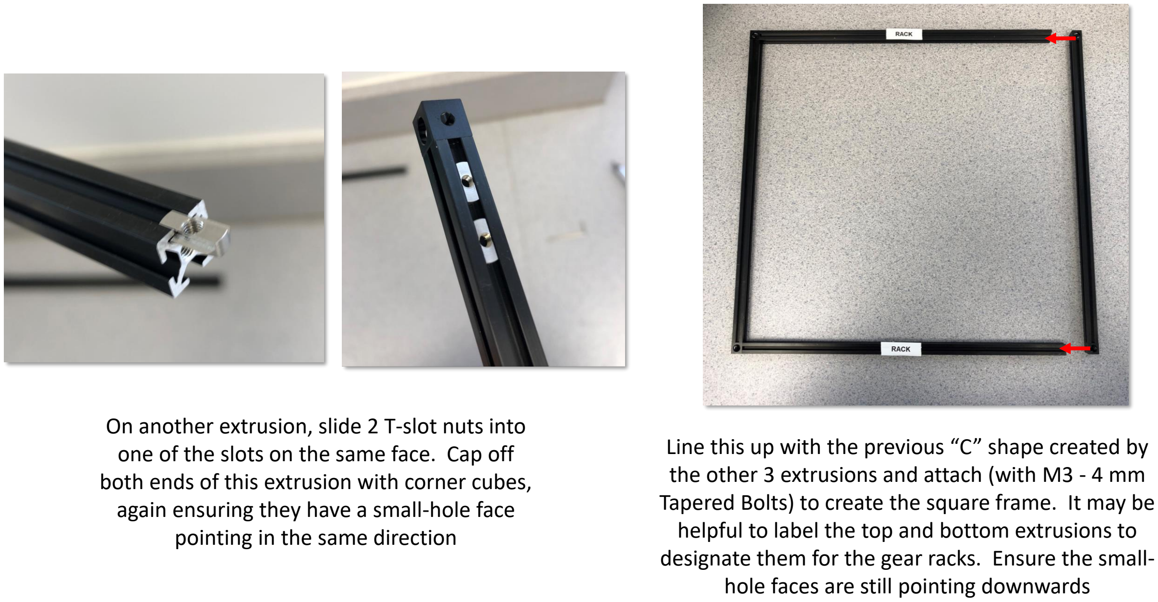
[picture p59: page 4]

On another extrusion, slide 2 T-slot nuts into one of the slots on the same face. Cap off both ends of this extrusion with corner cubes, again ensuring they have a small-hole face pointing in the same direction

Line this up with the previous “C” shape created by the other 3 extrusions and attach (with M3 - 4 mm Tapered Bolts) to create the square frame. It may be helpful to label the top and bottom extrusions to designate them for the gear racks. Ensure the small-hole faces are still pointing downwards

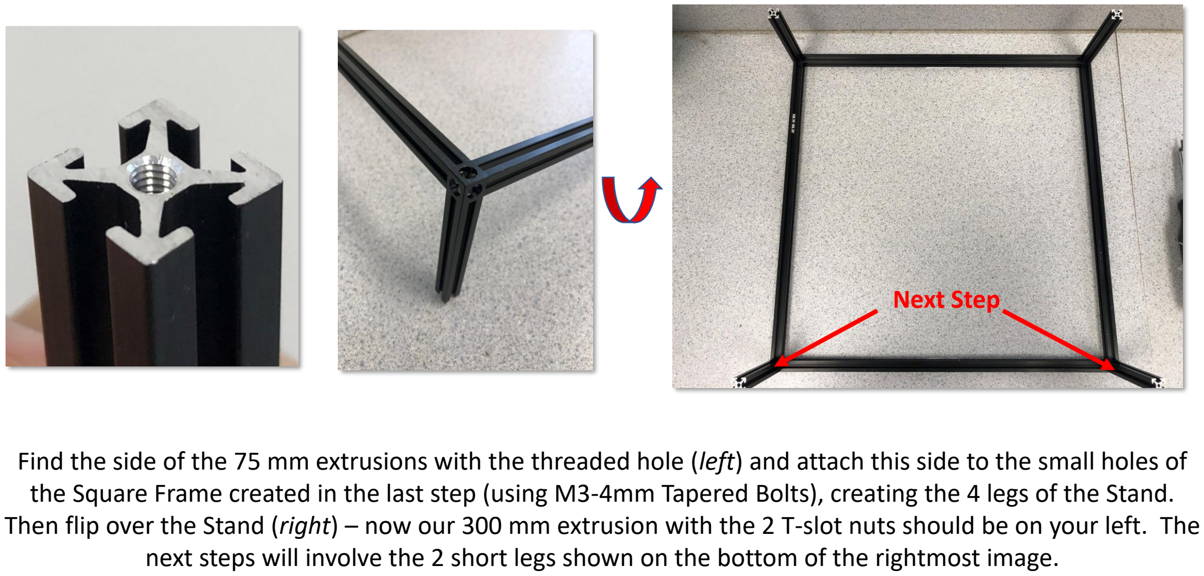
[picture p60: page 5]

Find the side of the 75 mm extrusions with the threaded hole (left) and attach this side to the small holes of the Square Frame created in the last step (using M3-4mm Tapered Bolts), creating the 4 legs of the Stand. Then flip over the Stand (right) – now our 300 mm extrusion with the 2 T-slot nuts should be on your left. The next steps will involve the 2 short legs shown on the bottom of the rightmost image.

Next Step

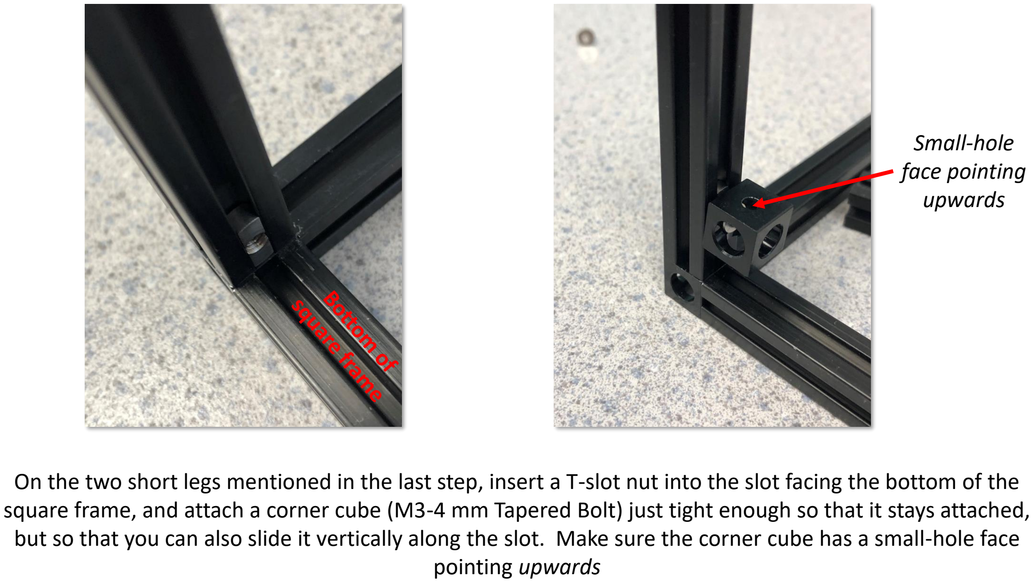
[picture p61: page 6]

On the two short legs mentioned in the last step, insert a T-slot nut into the slot facing the bottom of the square frame, and attach a corner cube (M3-4 mm Tapered Bolt) just tight enough so that it stays attached, but so that you can also slide it vertically along the slot. Make sure the corner cube has a small-hole face pointing upwards

Small-hole
face pointing
upwards

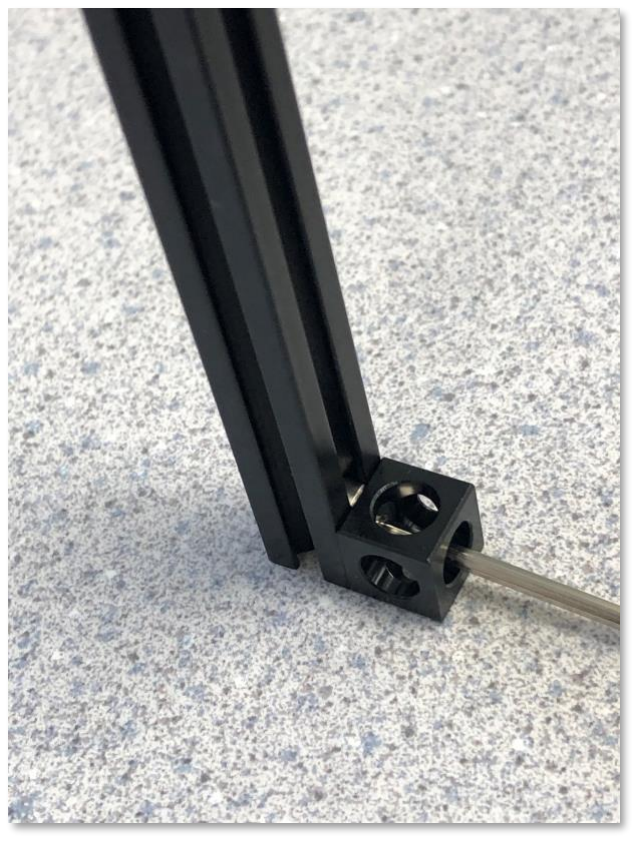
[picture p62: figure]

(Top Left) – Slide 2 T-slot nuts into a new 300 mm extrusion along the same face. Attach a Corner cube at both ends of the slot (M3-2mm Tapered Bolt) so that it lies flush with the end.

(Top Right) - To ensure it lies flush with the end, it can be helpful to hold the pieces as shown here when fastening them together. Ensure that there is a small-hole face pointing away from the end of the extrusion

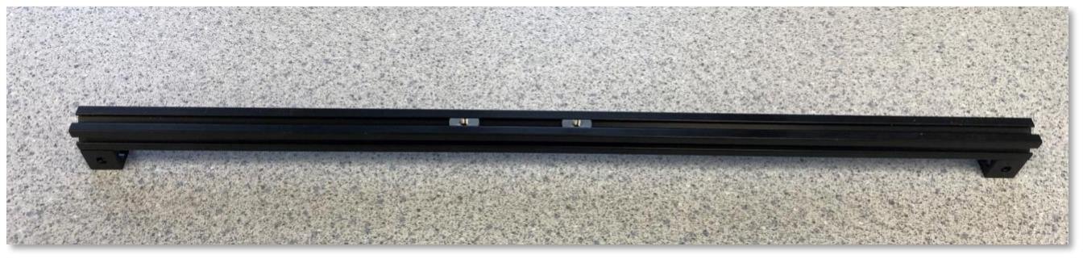
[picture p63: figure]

(Bottom) Flip this new assembly over, and insert two more T-slot nuts, ensuring that they don’t slide out as you move to the next step.

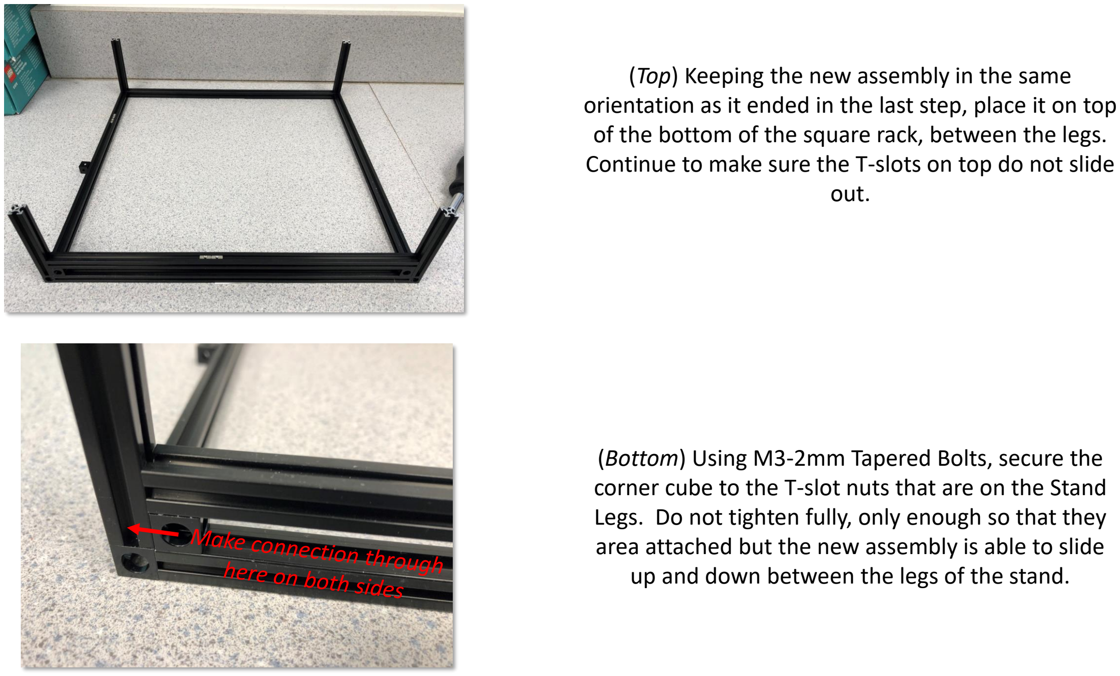
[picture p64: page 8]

(Top) Keeping the new assembly in the same orientation as it ended in the last step, place it on top of the bottom of the square rack, between the legs. Continue to make sure the T-slots on top do not slide out.

(Bottom) Using M3-2mm Tapered Bolts, secure the corner cube to the T-slot nuts that are on the Stand Legs. Do not tighten fully, only enough so that they area attached but the new assembly is able to slide up and down between the legs of the stand.

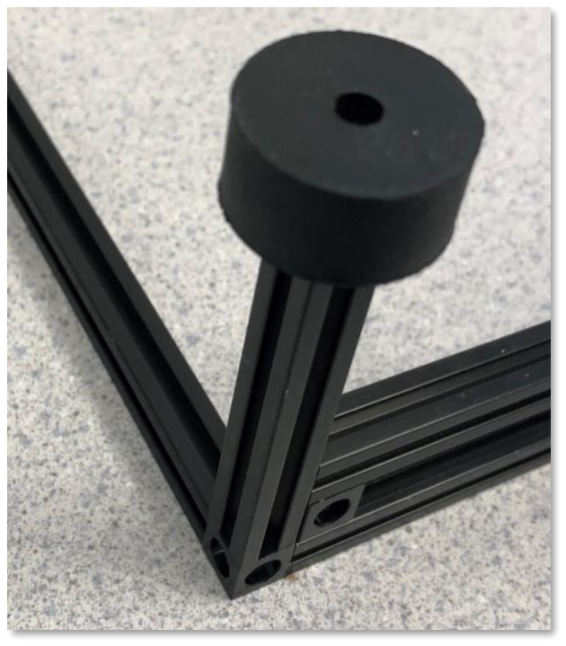
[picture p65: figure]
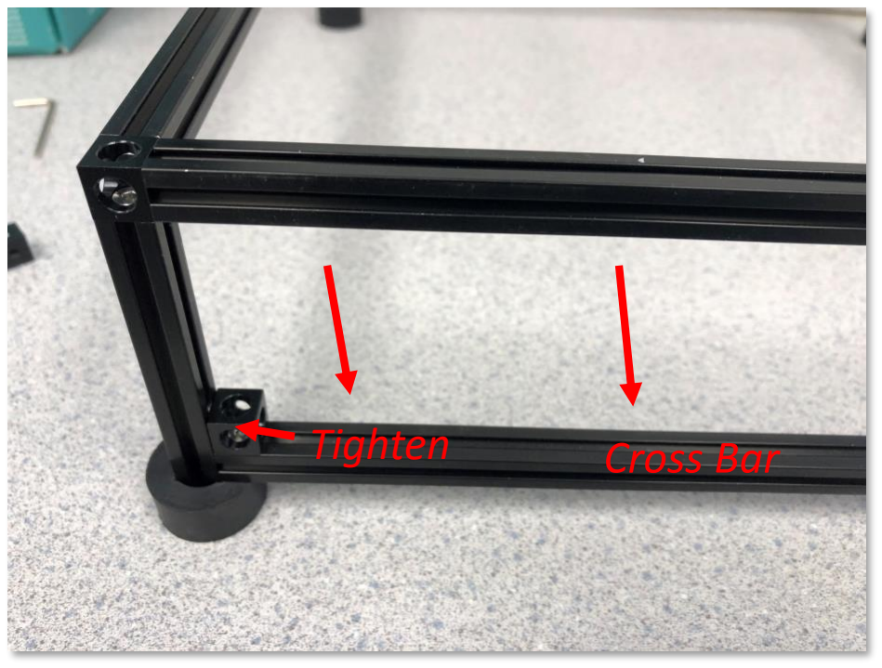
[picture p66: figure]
Cross Bar Tighten

(left) Place the Rubber End Caps (Or MakerBeam 3D Printed End Caps) on the end of each of the 4 legs.

(right) Flip over the frame, and now slide down the cross-bar assembly down so that it contacts the top of Rubber End Cap. Use the Hex Wrench to fully tighten the connection so the cross-bar does not move.

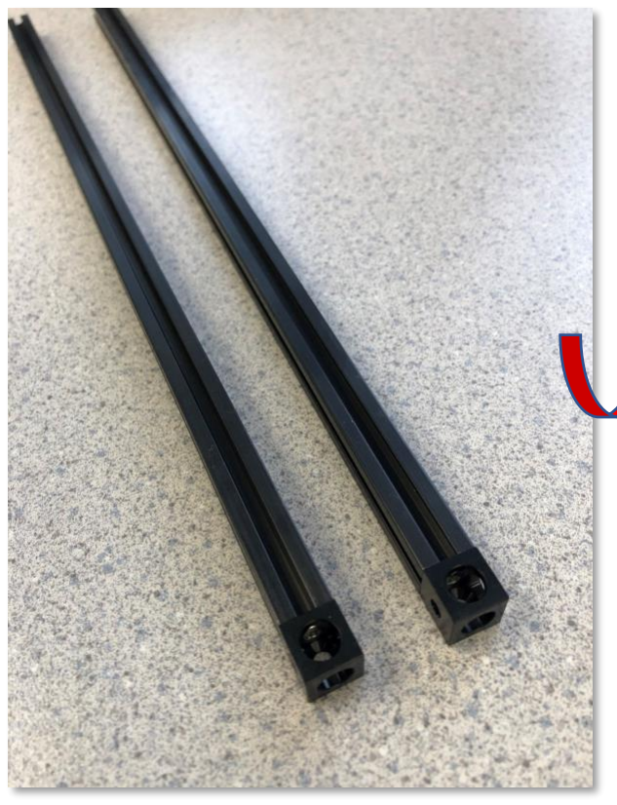
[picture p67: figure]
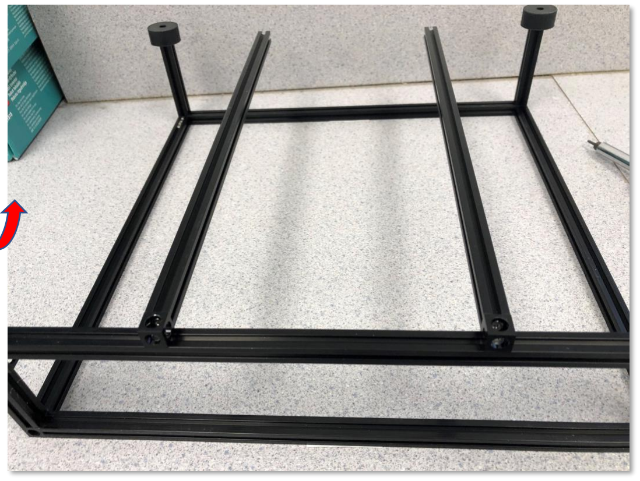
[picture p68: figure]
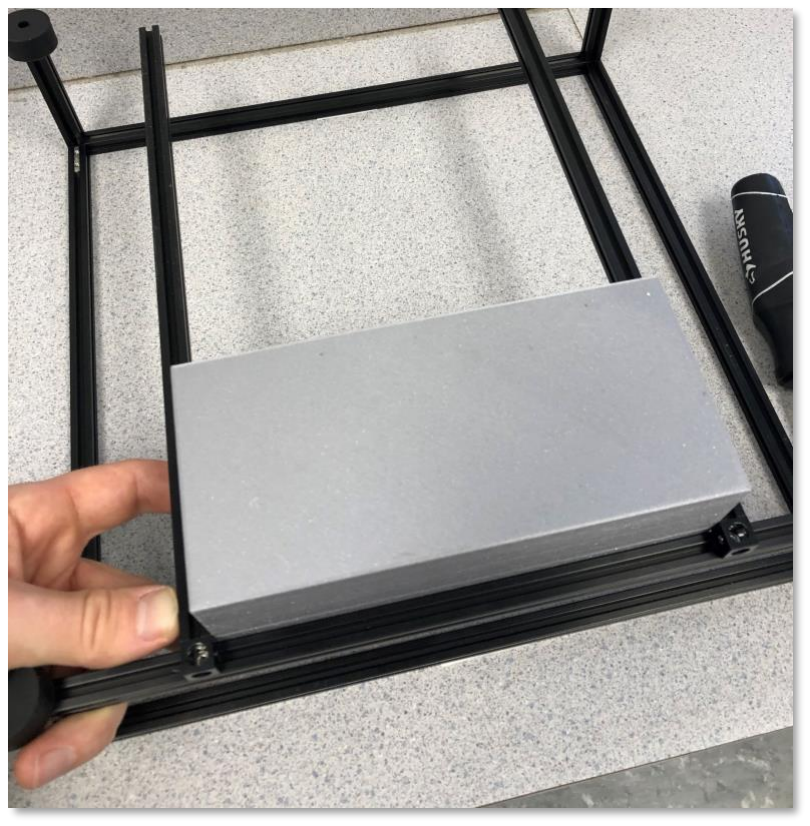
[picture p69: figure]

(left) Create two more Extrusions with Corner Cubes at the end (M3-4mm Tapered Bolts)

(middle) Flip over the frame again and attach each of these extrusions via their corner cube to the 2 T-slot nuts along the cross-bar assembly. Only tighten enough so they are attached but can slide left to right.

(right) Place the Acid/Base 3D Printed Reservoir between the two beams and slide them so they fit snugly against the sides of it. Now, remove the reservoir and tighten the beams where they are. These beams are here to keep the sample wells and reservoir steady during experiments; their position and width can be adjusted later.

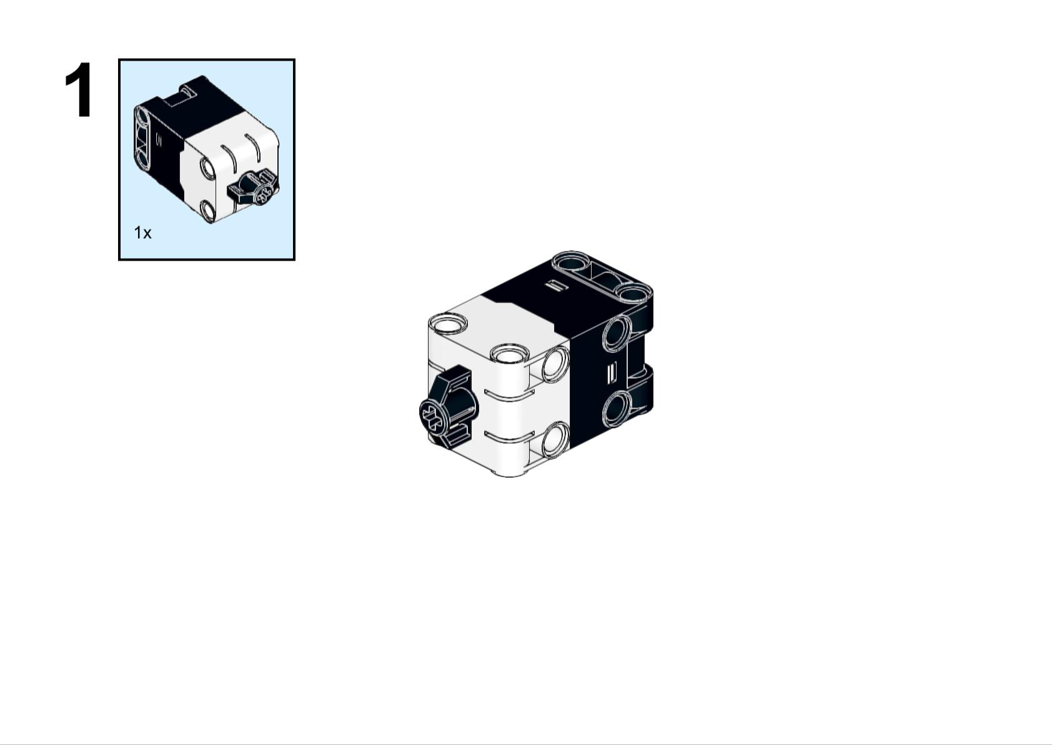
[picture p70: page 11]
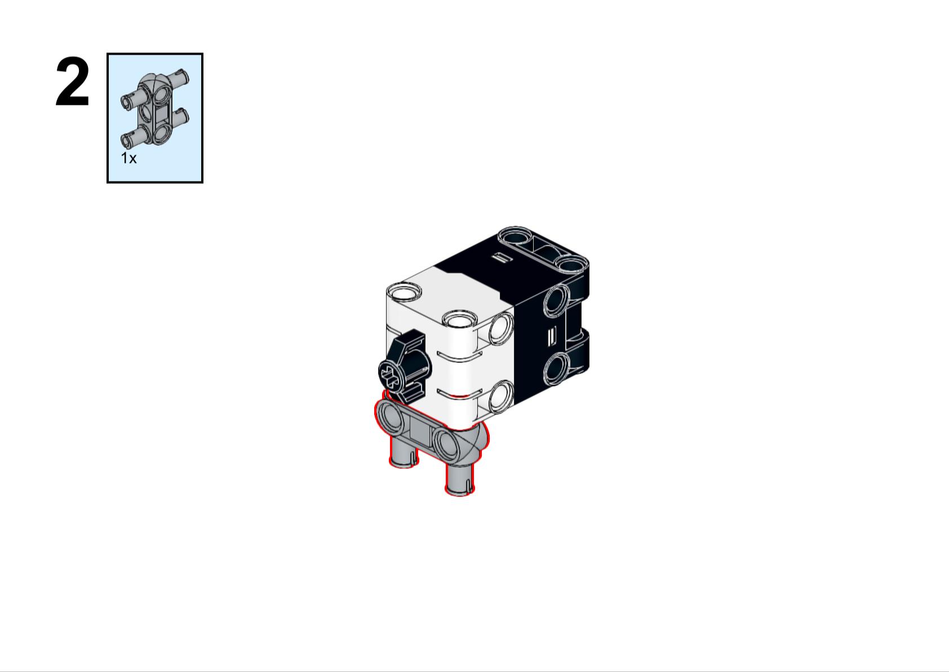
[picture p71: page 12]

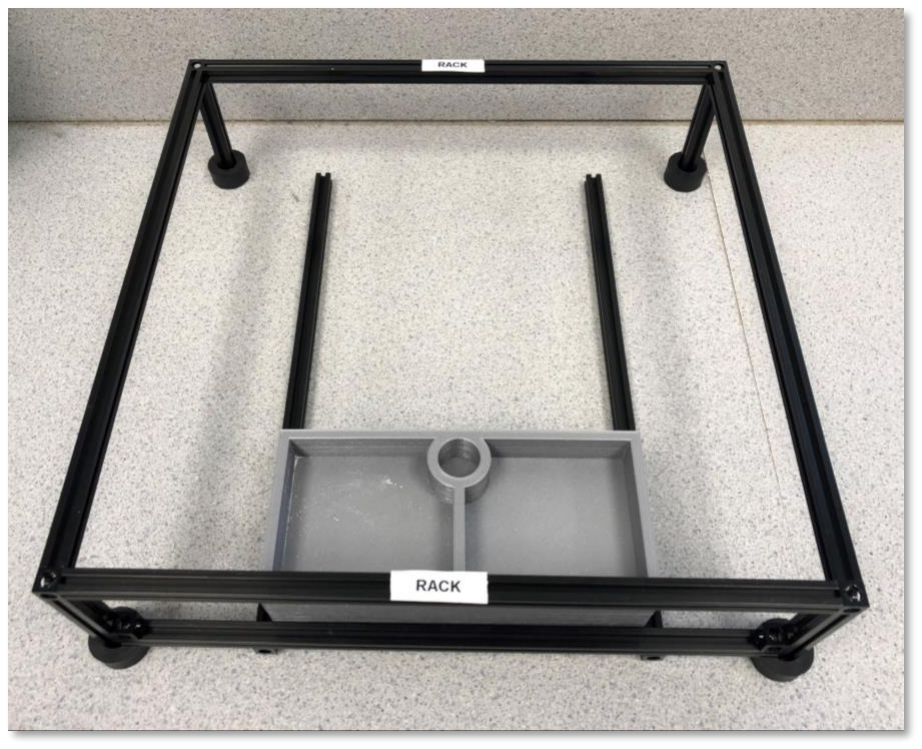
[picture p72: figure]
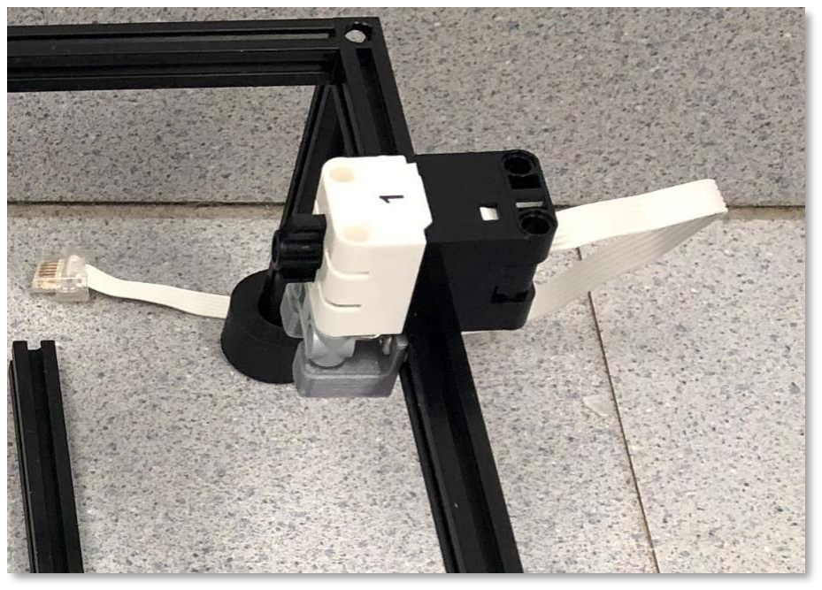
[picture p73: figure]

(left) Lightly loosen the two bolts securing the right-most extrusion of the square frame in this picture and rotate the entire extrusion clockwise, so that the T-slot nuts facing the ground are now facing the interior of the square.

(middle) Attach the Push Sensor Holder 3D printed pieces so that the LEGO holes are facing the floor. You can keep this connection loose enough so that you can move them around to the proper distance for the LEGO Push Sensor Assembly to fit.

(right) Attach the Push Sensor Assembly. Note that you should move this entire attachment (including the sensor) to a location along the extrusion in which the depressor will contact a mid-axle support from the gantry, but this can be done later.

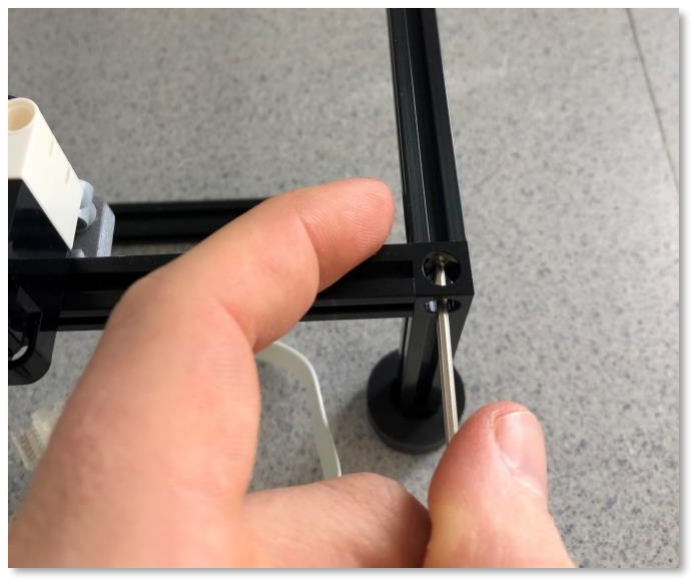
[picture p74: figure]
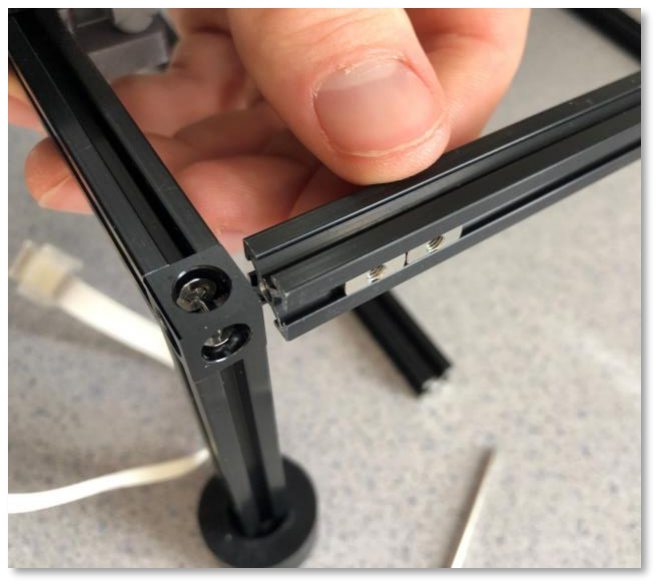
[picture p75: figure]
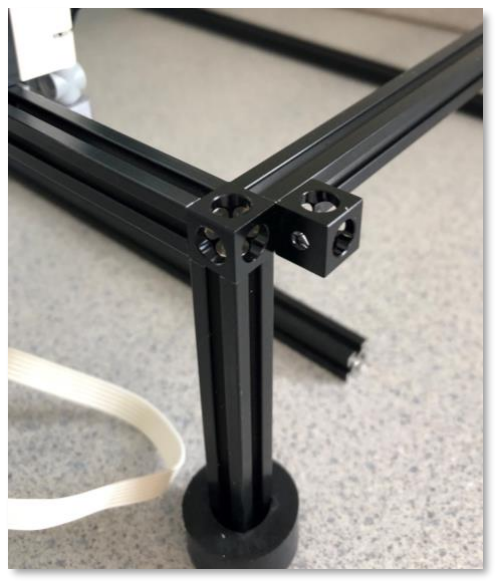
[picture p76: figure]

In this step we will install the End Stops on the frame, which prevent the robot from running off the track. Their spacing will be adjusted later (in the Bridge Instructions)

(left) Use a 2mm hex key to loosen the 2mm Tapered Bolt at one end of each “rack” designated extrusion

(mid-left) Pull the extrusion back, and slide 2 T-slot nuts into each extrusion

(mid-right) re-attach the “rack” extrusions, slide one of each T-slot nut to each end of the extrusion and secure a Corner cube so that it is locked in place. Do not overtighten (we will adjust their position along the extrusion later).

(right) at the end, there should be 4 corner cubes attached to the frame (2 per rack extrusion).


Now we will glue the LEGO rack pieces onto the frame on each “rack” designated extrusion.

(left) Deposit a small (1”) strip of superglue along the rack, placing the adhesive on both sides of the middle channel.

(mid-left) Place a rack piece down carefully, so that its end coincides with the end of the rack extrusion. Ensure it is parallel with the rack piece, and centered along its axis. Allow 30 seconds before applying the next 1” strip of superglue.

(mid-right) Repeat this process until one side of the rack is complete, ensuring there is no gap between pieces.

(right) Repeat again for the rack on the other side of the frame

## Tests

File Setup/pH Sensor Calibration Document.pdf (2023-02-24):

Autonomous Robot System Checklist (EV3)

## Calibration (pH Sensor)

IMPORTANT: The longevity of the pH sensor and the quality of the data it produces will be drastically reduced by leaving the probe exposed to the air or in a solution for an extended period of time (more than a few minutes). When it is not being used, keep the cap screwed on with enough of the electrode solution (1M KCl) so that the glass bulb is fully submerged.

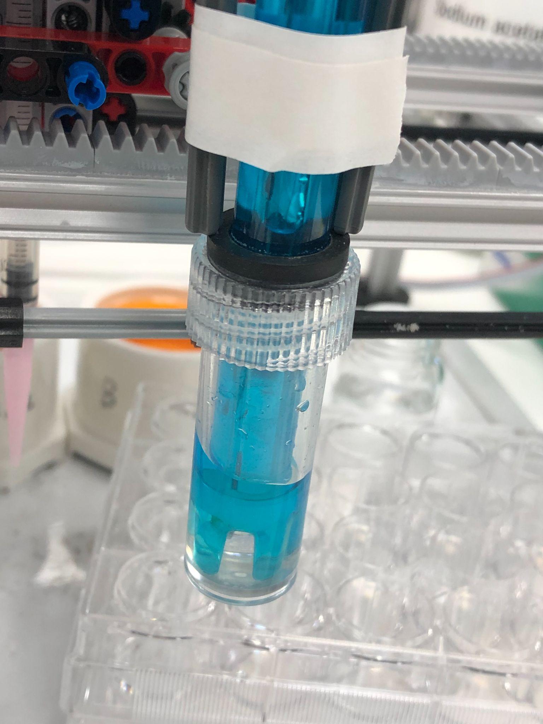
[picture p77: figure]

Fig. 12: When not in use, make sure that the cap containing electrode solution is screwed on and the bulb is fully submerged inside the solution.

The pH sensor is an electrochemical cell that returns a voltage value that is linearly proportional to the pH of the solution being measured. Calibration involves fitting a slope and intercept to this linear relationship so that a voltage value is associated with the correct pH. To do this, we will use buffer solutions. In this experiment, our pH values are expected to be between 4 and 7, so we do not need to calibrate outside this range (only need 2 point calibration).

1. Fill up some glass sample tubes with the color coded buffer solutions. DO NOT stick the pH sensor in the buffer solution reservoirs, as this can contaminate them.

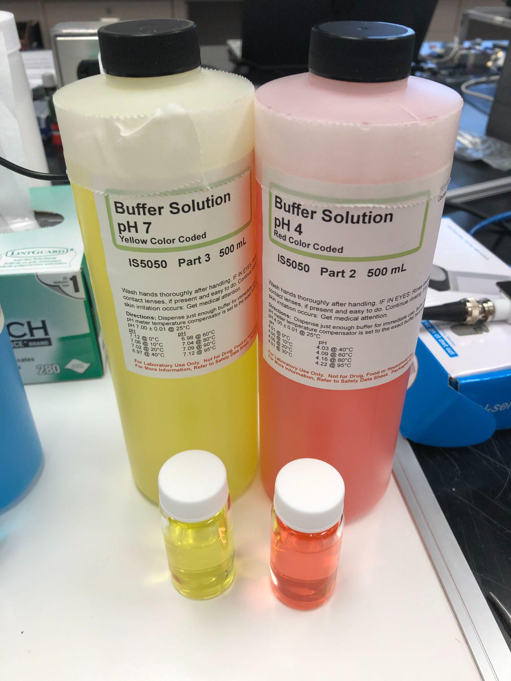
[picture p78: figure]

Fig. 13: Pour the color-coded buffer solutions in sample tubes before calibrating.

2. Make sure the pH meter is connected to the arduino as shown in the diagram below. Ensure the arduino is also connected by USB to your computer.

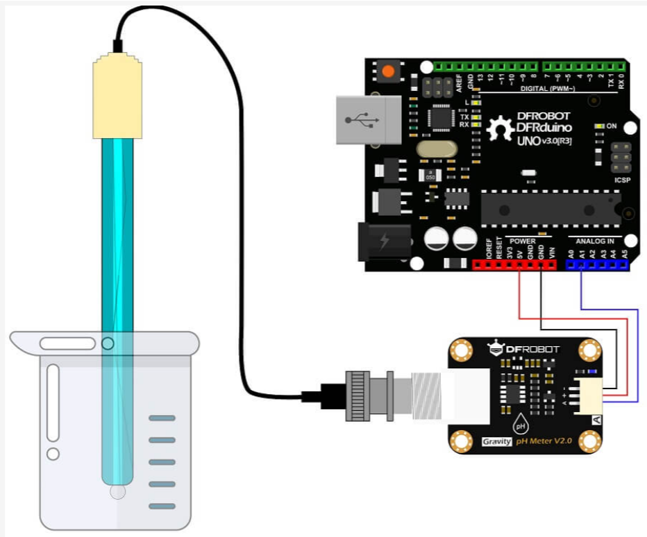
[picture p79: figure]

3. Open the code provided in the Arduino IDE, ensure it compiles, and upload it to the Arduino by identifying the correct port (you can check what port it is by going to Tools -Port , in the IDE).

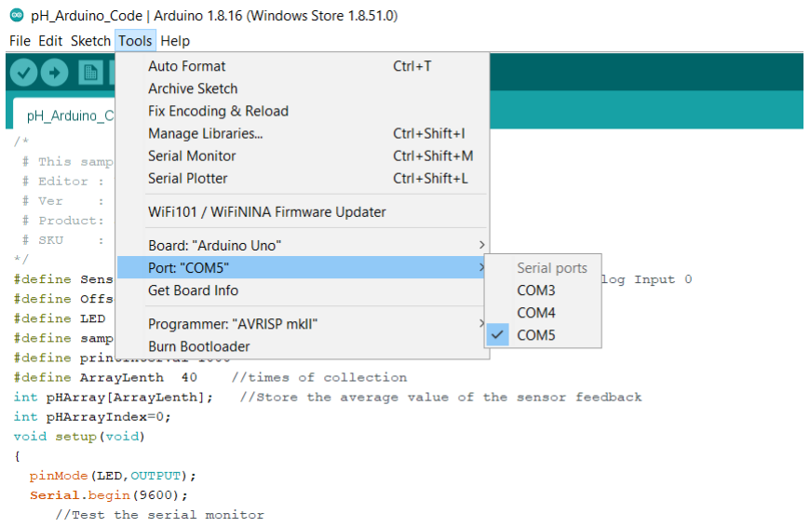
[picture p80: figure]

4. Press the arrow in the top left corner to upload the code to the Arduino. The code will output a pH value (calculated by multiplying the voltage by a slope, and adding an offset). Alter the code so that it prints the voltage instead. You can monitor the voltage by opening up the serial monitor (go to Tools - Serial Monitor )
It will print the voltage (a value from 0 - 2) about once every second.

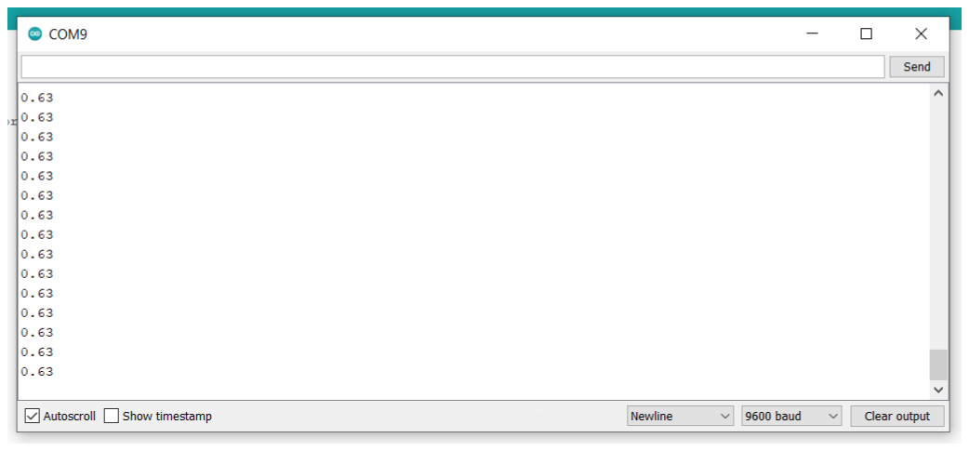
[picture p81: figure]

5. Raise one of the buffer solutions to the pH sensor and allow the bulb to be completely submerged for 15-30 seconds.

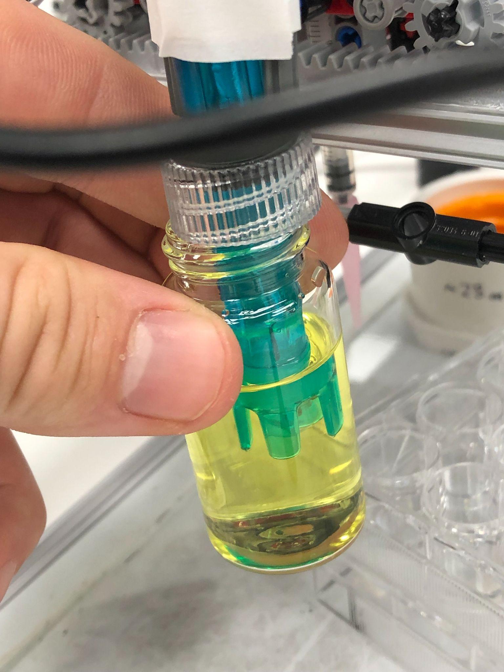
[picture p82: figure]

Fig. 17: Submerge the pH sensor in one of the buffer solutions, as shown.

Record the voltage from the serial monitor once the value stabilizes. Rinse the bulb in DI water for a few seconds and wipe lightly with a kim wipe to remove any moisture. Repeat this again with the other buffer solution and record that voltage. Use these values to determine the proper slope and offset that would return the correct pH values: Ex:
pH 4 Buffer Solution - 0.86 V pH 7 Buffer Solution - 1.79 V

Slope = (1.79 - 0.86)/(7-4) Offset = 4 - slope*0.86

Replace the slope and Offset values in the code. Then alter the code back so that it prints out ONLY the pH.

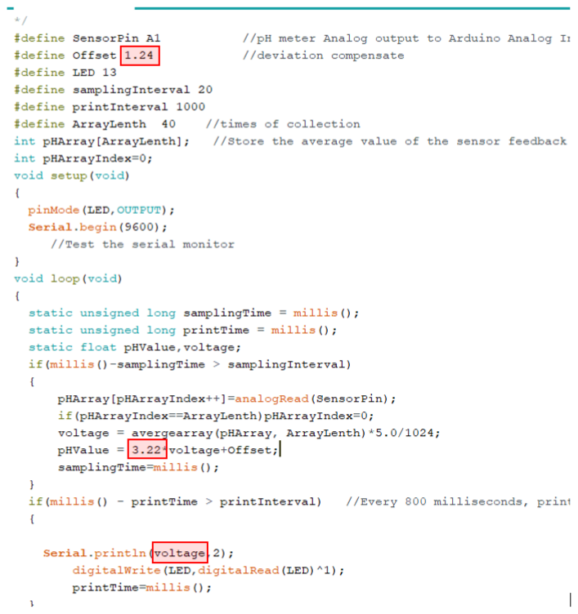
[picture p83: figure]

Figure 18: Location of the offset, slope, and print values in the code. Alter “voltage” so it says “pHValue” instead

You can reconfirm that the pH meter is performing well by looking at the serial monitor and immersing the sensor in the solutions again.

Reupload the code to the arduino and then make sure you close the serial monitor and IDE. (if you don’t you won’t be able to monitor the serial port from your jupyter notebook.

6. Replace the COM PORT with the correct one in your jupyter notebook (corresponding to the arduino). Make sure to close the port after defining it. (ser.close()).

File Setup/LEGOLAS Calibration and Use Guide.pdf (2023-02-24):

# LEGOLAS Calibration and Use Guide

# The LEGOLAS System

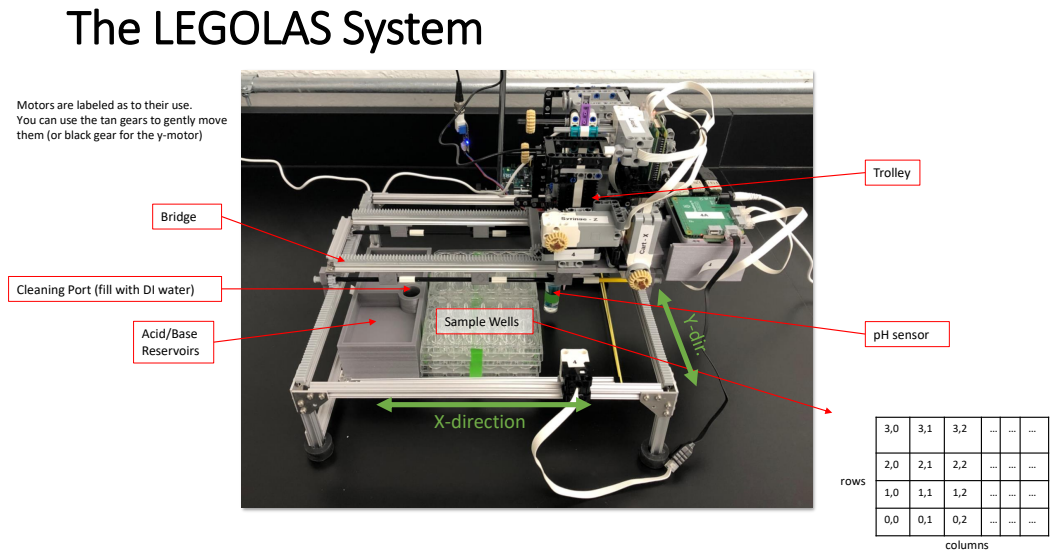
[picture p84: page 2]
Sample Wells; Acid/Base Reservoirs; Bridge; Trolley; pH sensor; rows; columns; X-direction

Motors are labeled as to their use.
You can use the tan gears to gently move
them (or black gear for the y-motor)

Cleaning Port (fill with DI water)

# Wire Management

columns

Each LEGOLAS had a chemistry stand with a ring behind it to raise up the pH sensor wire. If you are having problems with wire management, please consult the Wiring Guide to see the optimal setup. Most problems are due to the pH sensor wire getting caught and not allowing the sensor to drop, which can be fixed by giving it more slack, as well as identifying where it is getting caught and moving it away from that area prior to an experiment.

# To Do

1

st Time using LEGOLAS
- Connect to Wifi Router
- Install Anaconda w/ Jupyter Notebooks
- Download and unzip necessary files

Every Time you use LEGOLAS
- (Re)calibrate LEGOLAS (or at least verify calibration)
- Remove pH sensor cap prior to using
- Do not knock cart off tracks!! (or you might have to recalibrate )
- Return pH sensor cap after using

Before Final Experiments:
- Calibrate pH Sensor using buffer solutions and Arduino Code

1

# st Time: Connect to Wifi Router

The wifi router is located in the back of the lab.

# Name: TP-Link_BC08 Key: 98043828

# Note: We use a local wifi router because the school blocks use on eduroam. If you need access to the internet on the same device you are using to control LEGOLAS, you will have to switch back to eduroam. You can only control LEGOLAS if you are connected to the TP-Link local

network.

1

# st Time: Install Anaconda

# Please download and install Anaconda: https://www.anaconda.com/products/individual

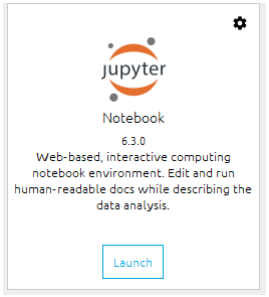
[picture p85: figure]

# Run Anaconda Navigator and then launch Jupyter Notebook (install if needed) - This will

open a page in your browser.

1

# st Time: Download Files

## Download the Use Files from github - manual.py (use to calibrate LEGOLAS)

## - Once calibrated, export as “config.yaml“ to serve as configuration file - You will likely update config.yaml every time you come to the lab

## - core.py (contains movement and deposition functions for reference) - ref_config.yaml (reference config file, will be replaced by config.yaml) - LegolasDemo.ipynb (Demo to test calibrated values) - LegolasOutline.ipynb (Template for solving challenges)

## You will use the “Anaconda Prompt” to access and utilize manual.py You will edit LegolasDemo.ipynb & LegolasOutline.ipynb in Jupyter notebooks which you can launch from the “Anaconda Navigator” screen

# Every Time you Use LEGOLAS

## - The following slides show how to calibrate and set up LEGOLAS, which you will need to do every time you use it and will have to redo if you knock the cart off the tracks in the x or y direction (or if you move the sample wells/reservoir). Therefore, it is in your best interest to be careful with

how you interact with LEGOLAS once you have set it up.
- You should conduct the steps in the order they appear in this ppt.

Tips: - Adjust motors using the tan gears (or large black gear for y-direction) - Ensure that the pH meter and/or syringe are in the “full_up” position before manipulating the carts x & y position (to prevent collisions with sample wells) - Run the code blocks in LegolasDemo.ipynb to ensure calibration has been done correctly

# Access Calibration Window

# - Search in your windows search bar for “Anaconda Prompt” and open it - Go to the location or of the folder containing your files and copy the “PATH” (ex: C:\Users\logan\Documents\legolas_files) - In the prompt, type: cd PATH (insert your “PATH” here)

## - Now you are in the proper file directory

# - Type: python manual.py

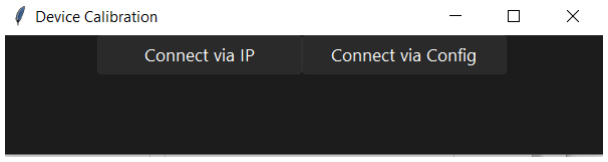
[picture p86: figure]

Prompt Example

This should appear

# Initial Physical Adjustments

# - (1) Before moving on with calibration:

## - Unscrew the cap of the pH sensor - Gently slide off the gasket and top - Place aside, being careful not to spill the cap with the electrode storage solution

- if you do spill, there is extra storage solution, just ask a TA.
- You need to assure there is enough solution in the cap prior to putting it back on, or else

### the electrode may dry out and not be useful (bulb must be submerged in solution)

## - Use the yellow gears for the “Syringe-Z” & “pH-Z” motors to move the z-height of the syringe and pH sensor above that of the sample wells

# - (2) Adjust the “liquid” motor so that the syringe plunger is at the

bottom (i.e. no liquid in syringe).

# Initial Physical Adjustments (Pics & Video)


(1) (2)

Syringe
Plunger is
fully down
(black)

Video: (https://youtube.com/shorts/YAqeFvSTQog?feature=share) removing cap
and gasket-top, then
raising pH sensor
and syringe out of
the way of sample
wells

Note:
Be careful not to
squeeze the end of
the pH sensor or it
will break as it is
brittle

# Connecting to the Raspberry Pi’s

For the first time you connect to the 2 raspberry Pi’s on your LEGOLAS,

# use the “Connect via IP” option

## - After you have completed this once, you can select your exported .yaml file when you click “Connect via Config” (then you can continue to calibrate from there)

When prompted for R Pi 1 IP Address, use the IP address for “Group#A”, and use “Group#B” for R Pi 2.

1A: 192.168.0.2
1B: 192.168.0.3

2A: 192.168.0.4
2B: 192.168.0.5

3A: 192.168.0.6
3B: 192.168.0.7

4A: 192.168.0.8
4B: 192.168.0.9

IP Addresses

# General Calibration Usage


Once you have connected to the Raspberry Pi’s and adjusted the physical system, you should see the calibration screen (shown right)
- Pos: shows the position (in degrees) of each motor & this will update if you move the motors via the keyboard controls or manually
- Speed: is the speed at which the motors will move if you use the keyboard controls (suggested to keep at 80)
- Keyboard Controls (press ctrl + M to access) – Not Recommended:
- pH Sensor - Z: (1 = up, 2 = down)
- Syringe - Z: (Q = down, W = up)
- Syringe Plunger (Liquid): (E = down, R = up)
- Cart-X: ( = left, → = right)
- Gantry-Y: (up arrow = up, down arrow = down)
- Manual Controls (Recommended):
- You can use the tan or black gears to manipulate the motors yourself
- This gives a higher degree of control, as the keyboard controls are not the best
- The motors will update their position when you move them this way as well, but be careful not to knock the cart off the tracks

# Home Calibration

Make sure the gantry is perfectly perpendicular to the base frame and that the gears sit in the teeth of the rack for both the gantry and cart assemblies

Select “Home” in the calibration window, and this screen will appear:


Set x offset and y offset to -100. These define the number of degrees the x and y motors will backtrack once they have contacted the push sensors on their axis. This helps create a reference position for all further calibration steps.

Press “home” and see the LEGOLAS glide down the x and y axis and then come to a rest.

From here on out, you do not want to knock LEGOLAS off the tracks or you will likely have to restart…

# pH device Calibration

Select “pH device” in the calibration window, and this screen will appear:


Use the x & y motor manual operation gears to align the pH sensor guide tube (grey cylinder) above the 0,0 cell (see slide 2 for sample well numbering). The pH sensor should be up inside the tube currently.
Use the manual operation gear on the motor labeled “pH-Z” to lower the pH sensor into the well so that it is just touching the bottom of the well (not too much slack on the line)
- Under “Name,” select “full_down” and click “Enter”. This sets this position as the lowest point that we will lower the sensor to
Again using the manual operation gear, raise the pH sensor up so it is just back in the tube again
- Select “full_up” and click “Enter”
You can reselect full_up or full_down and click “Goto” to test your calibrated values
Manually or through the “Goto” function, ensure the pH sensor gets lifted out of the cells so you can move onto the next steps without it colliding with the sample wells…

# pH device Calibration (Video) (https://youtu.be/-re3mjaBBEA)


Testing full_down
and full_up using
the “Goto” button
after the values
have been set

# Deposition Device (Syringe) Calibration

Select “depo device” in the calibration window, and this screen will appear:

Calibrating the syringe is similar to that of the pH device


Use the x & y motor manual operation gears to align syringe above the acid or base reservoir.
Use the manual operation gear on the motor labeled “Syringe-Z” to lower the syringe into the reservoir as far as possible.
- Under “Name,” select “full_down” and click “Enter”. This sets this position as the lowest point that we will lower the syringe to
Again using the manual operation gear, raise the syringe up so it is as high as possible.
- Select “full_up” and click “Enter”
You can reselect full_up or full_down and click “Goto” to test your calibrated values
Manually or through the “Goto” function, ensure syringe gets lifted out of the reservoir so you can move onto the next steps without it colliding with the sample wells…

# Device offset Calibration


We will now create a value for the device “offset,” or distance between the pH sensor tip and syringe tip in the x and y directions.
Select “depo device” in the calibration window, and this screen will appear:
We will define the pH sensor as the “stage” and align this again with the 0,0 sample well. To make sure it is fully aligned, you can reopen the pH device calibration window and select full_down to see if it aligns correctly.
Once it is aligned with the 0,0 well, press “Enter” for both “Stage Center” and “pH”
Ensure the pH sensor is lifted to full_up, and then manually move the syringe so it is aligned with the direct center of the 0,0 well.
Now click “Enter” for “depo”

# Stage Calibration

We will now map out important areas in the experiment space, using the pH sensor as the alignment point (device offset from the prior step will allow us to align the syringe when needed).


Select “stage” in the calibration window, and this screen will appear:
Move the pH sensor guide tube above the leftmost reservoir (any point above it)
- Enter “acid” in the “Name” bar and click Enter
Move the pH sensor guide tube above the rightmost reservoir
- Enter “base” in the “Name” bar and click Enter
Move the pH sensor above the cleaning reservoir (use full_up & down if needed to align)
- Enter “base” in the “Name” bar and click “Enter”

# Cell Calibration

Now we will map out the sample wells, again using the pH Sensor as our alignment point. We are only using the bottom 4 x 6 sample wells for any experiments you will be conducting.
Enter “4 6” in Cell Size and click “Enter”
Align the pH sensor with the 0,0 sample well (bottom left corner)
- In “Key Position,” enter “0 0” and click enter
Move the pH sensor to the 3,0 sample well (top left)
- In “Key Position,” enter “3 0” and click enter
Move the pH sensor to the 3,5 sample well (top right)
- In “Key Position,” enter “3 5” and click enter
Move the pH sensor to the 0,5 sample well (bottom right)
- In “Key Position,” enter “0 5” and click enter


Now select “Auto Fill” and “Show” to see that you have mapped out the 24 cells (they will appear solid white) Use “Goto” and fill out arbitrary row and column numbers in “Key Position” to test your calibration
It is suggested you lower the pH sensor into each well for every point to ensure it is a proper location in the x & y. (The pH sensors are close in size to the sample well so if you are off by even a little bit it may be hindered in lowering).

# Deposition Volume Calibration

Select “depo volume” in the calibration window and you will see this window (enter V/W as 1):
- V/W = 1 because… 1 g of water = 1 mL of water
Set up the scale with the orange cap (full to brim with water) to the right of the sample wells. Align the syringe (with plunger fully down) with the cap and place the tip into the water.
Zero the scale (press the T button).


In small increments (approx. 0.1 grams at a time), raise the syringe plunger using the “Liquid” motor with the manual operation gear (tan).
At each increment, record the exact Weight in grams as a positive number (it will be negative on the scale) and select “Enter.” Do this for at least 6 points up to 0.7 grams of liquid (0.6 grams is the most we will be taking up at one time in our experiments).
You can press “Clear” if you mess up and want to redo the calibration.
Make sure to deposit the liquid back into the cap at the end, and let another group use the scale, as we only have one at the moment.

Deposition Volume Calibration (Video) (https://youtube.com/shorts/3P0gzAvriLA?feature=share)


# Packing up the LEGOLAS

At the end of each session using the LEGOLAS, it is important to take the 3D printed reservoir and sample wells to the sink and dump out and solution/DI water. This will prevent contamination in further experiments. You can remove these easily by removing the rubber band around the sample holder posts, and then sliding the wells and reservoir out.

You must also place the gasket-top of the pH sensor on and then screw on the cap (with sufficient electrode storage solution so that the bulb is submerged). This can be a little difficult so do not hesitate to ask a TA for help so that you do not break the pH sensor tip. The video below shows one way to approach placing it back on. DO NOT pull on the blue section or squeeze its tip while trying to put everything back on. Rather, use the wire above the pH sensor for leverage while putting the cap back on.

# Before Final Experiments (Calibrating pH)

The pH sensor measures a voltage across two electrodes that is linearly related to the pH of the solution. Before conducting a final experiment, you want to conduct a 2 point calibration of this relationship using the buffer solutions provided in the lab.

Refer to the pH Sensor Calibration Document for information on how to do this. Feel free to ask a TA for help if needed.

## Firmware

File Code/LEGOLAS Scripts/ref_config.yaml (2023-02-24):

devices:
  depo:
    s_positions:
      full_down: -246
      full_down_re: -289
      full_up: -34
    vol_deg_map:
      0.0: -177
      0.193: -8
      0.38: 140
      0.747: 433
    x_offset: -53
    y_offset: -195
  pH:
    pH_positions:
      full_down: 1884
      full_up: 2081
    verbose: true
    x_offset: 0
    y_offset: 0
global:
  pi1_address: 192.168.0.2
  pi2_address: 192.168.0.3
stage:
  aux_loc_map:
    acid:
    - -1313
    - -120
    base:
    - -1326
    - -717
    clean:
    - -1136
    - -421
  cell_loc_map: C:\Users\auror\Desktop\legolas\cell_map.pkl
  home_x_offset: -100
  home_y_offset: -100

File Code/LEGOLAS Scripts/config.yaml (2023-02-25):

devices:
  depo:
    s_positions:
      full_down: -237
      full_up: 52
    vol_deg_map:
      0.0: 0
      0.5: 200
      0.7: 300
    x_offset: -63
    y_offset: -189
  pH:
    pH_positions:
      full_down: -407
      full_up: -103
    verbose: true
    x_offset: 0
    y_offset: 0
global:
  pi1_address: 192.168.0.2
  pi2_address: 192.168.0.3
stage:
  aux_loc_map:
    acid:
    - -1319
    - -127
    base:
    - -1319
    - -656
    clean:
    - -1142
    - -427
  cell_loc_map: C:\Users\logan\Documents\Fall 2022\Research\LEGOLAS Project Files\LEGOLAS
    Files\cell_map.pkl
  home_x_offset: -100
  home_y_offset: -100

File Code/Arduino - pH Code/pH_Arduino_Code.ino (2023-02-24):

/*
 # This sample code is used to test the pH meter V1.0.
 # Editor : YouYou
 # Ver    : 1.0
 # Product: analog pH meter
 # SKU    : SEN0161
*/
#define SensorPin A0           //pH meter Analog output to Arduino Analog Input 0
#define Offset 0.75            //deviation compensate
#define LED 13
#define samplingInterval 20
#define printInterval 1000
#define ArrayLenth  40    //times of collection
int pHArray[ArrayLenth];   //Store the average value of the sensor feedback
int pHArrayIndex=0;
void setup(void)
{
  pinMode(LED,OUTPUT);
  Serial.begin(9600);
     //Test the serial monitor
}
void loop(void)
{
  static unsigned long samplingTime = millis();
  static unsigned long printTime = millis();
  static float pHValue,voltage;
  if(millis()-samplingTime > samplingInterval)
  {
      pHArray[pHArrayIndex++]=analogRead(SensorPin);
      if(pHArrayIndex==ArrayLenth)pHArrayIndex=0;
      voltage = avergearray(pHArray, ArrayLenth)*5.0/1024;
      pHValue = 3.37*voltage+Offset;
      samplingTime=millis();
  }
  if(millis() - printTime > printInterval)   //Every 800 milliseconds, print a numerical, convert the state of the LED indicator
  {

    Serial.println(pHValue,2);
        digitalWrite(LED,digitalRead(LED)^1);
        printTime=millis();
  }
}
double avergearray(int* arr, int number){
  int i;
  int max,min;
  double avg;
  long amount=0;
  if(number<=0){
    Serial.println("Error number for the array to avraging!/n");
    return 0;
  }
  if(number<5){   //less than 5, calculated directly statistics
    for(i=0;i<number;i++){
      amount+=arr[i];
    }
    avg = amount/number;
    return avg;
  }else{
    if(arr[0]<arr[1]){
      min = arr[0];max=arr[1];
    }
    else{
      min=arr[1];max=arr[0];
    }
    for(i=2;i<number;i++){
      if(arr[i]<min){
        amount+=min;        //arr<min
        min=arr[i];
      }else {
        if(arr[i]>max){
          amount+=max;    //arr>max
          max=arr[i];
        }else{
          amount+=arr[i]; //min<=arr<=max
        }
      }//if
    }//for
    avg = (double)amount/(number-2);
  }//if
  return avg;
}

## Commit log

2023-02-15 Create 3D Printing
2023-06-09 utils to manage the raspberry pi
2023-06-16 Update manual.py
    Added code to undo motor lockup as soon as you load into manual.py writes coast to the motors which fixes the issue
2023-06-19 fix-ish. send command to release the motor
2023-06-20 add lines to unlock the motor once connected
2023-06-20 experimenting with the motor off
